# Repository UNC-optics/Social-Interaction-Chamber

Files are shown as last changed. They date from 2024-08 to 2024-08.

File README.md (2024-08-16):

# Detailed Protocol: Social Interaction Chamber 

See the *Detailed Protocol* tab in the *Materials List/Social Interaction Chamber Materials.xlsx* spreadsheet for a sequential list of the required materials for the construction of the Social Interaction Chamber.

GitHub repository: https://github.com/UNC-optics/Social-Interaction-Chamber 

# Construction of laser cut box

1.	Use the *Hardware Manufacturing/Laser Cutting Files/Social Interaction Chamber Walls Laser Cut File.svg* file to vector laser cut the structural panels of the Social Interaction Chamber.
   
2.	Cut the partition and lid (black lines) out of 1/16in clear cast acrylic.
   Clear Laser Cut Pieces
  	
3.	Cut the left and right walls, back wall, and floor (red lines) out of 1/8in white cast acrylic.
   White Laser Cut Pieces
  	
4.	Use acrylic paste cement to attach the walls and floor. Leave the lid and partition detached from the rest of the panels.
   
5.	Use acrylic paste cement to secure the acrylic hinge to the lid and the back wall of the box.
   Chamber Acrylic Assembly

6.	Allow acrylic panels to sit overnight to cure. 

# PCB assembly

7.	Use the *Hardware Manufacturing/PCB Fabrication and Assembly/PCB Fabrication Files Social Interaction Chamber.zip* folder provided in the GitHub to order the custom pre-assembled PCB from a manufacturing company (JLCPCB, HK, CN). The PCB should be prepared as a 1.6mm thick two-layer PCB, with no special instructions.
   
8.	In the same order, use the *Hardware Manufacturing/PCB Fabrication and Assembly/PCB Assembly Files Social Interaction Chamber.zip* folder to request electronic component assembly services. Parts must be placed according to the Bill of Materials and Components Placement List as demonstrated in the assembly files.
    
9.	Following assembly, use a tampered cutter tool to detach the PCB board at the indicated joints to produce 2 L-shaped PCBs and one rectangular PCB.
   PCB PreCut

10. Hand solder the 90-degree pins onto the rectangular PCB as shown.
    PCB PostCut

11. Solder the base of the L-shaped PCBs to the other end of the 90-degree pins to hold them perpendicular to the rectangular PCB. Use the width of the acrylic chamber as a sizing guide and ensure that the diodes of the L-shaped PCBs face inward toward one another with the flush side of the base PCB facing upward.

    PCB Perpendicular

12. Use the tampered cutter tool to trim the excess wire from the 90-degree pins.

# PCB testing and cable construction

13. Plug in a USB-A to USB-C cable into the Seeeduino XIAO and a computer with Arduino IDE software (Version: 2.3.2). Install the Seeeduino library and drivers via the board manager (https://wiki.seeedstudio.com/Seeed_Arduino_Boards/).
    
14. Open the *Microcontroller Programming Code/Programming_Code_Social_Interaction_Chamber.ino* file using the Arduino IDE software. Connect to the Seeeduino XIAO port and allow the device to sit freely without obstructions. Upload the programming code to the board.
  
15. Open the serial monitor in the Arduino software. Obstruct the beam path with a solid object and ensure that Inside “I”, Outside “O”, and Near “N” outputs appear in the serial monitor along with binary data indicating beam break status (0 - no break, 1 - beam broken). Upon functionality confirmation, unplug the device.
    
16. Use wire strippers to remove ~20mm of the outer jacket from one end of the black cable and expose the 4 internal conductors. Then strip ~10 mm of insulator from each of the individual wires to expose the copper core of all internal conductors.
    
17. Thread heat shrink over each of the 4 internal conductors. Hand solder the wires on one side of the cable to each of the metal pins of the 4-pin female socket header as shown in Figure 2B. Pull the heat shrink over exposed wire surfaces and melt the material with a soldering iron to enclose the soldered junctions.
    
    Cable Pinout

18. On the other end of the black cable, use the wire stripper to remove ~50mm of the jacket and ~15mm of insulator from each internal conductor. The open wires will be secured into the ANY-maze digital interface terminals in the experimental protocol.

# 3D printed case and waterproofing
19. 3D print the PCB case and diode sleeves provided in the *Hardware Manufacturing/3D Printed Parts* folder using white PLA filament with 0.2mm resolution.
20. When the print is complete, use tweezers to remove internal supports from the diode sleeves and the PCB case.
    3D Printed Casing
    
21. Place the external PCB case over the finalized PCB to protect the PCB and components.
PCB with Case

22. Fit the PCB around the acrylic walls with the diodes aligned with the 4 holes through each wall. Be sure to avoid dragging the diodes across the edge of the wall to prevent damage.
    
    PCB Placed Around Chamber

23. Super glue the 3D printed inner diode sleeves to the internal wall of the chamber.
    Inner Diode Sleeve Placement

24. With a 1:1 ratio, mix 20mL of 2-part epoxy. If a 1:1 ratio is not maintained, the epoxy will not fully cure.
25. Use a cotton swab to apply the mixed epoxy into the space between the PCB and the external casing, as well as along the bottom edge of the chamber and PCB. Be generous along this surface and over the PCB, as it will waterproof the chamber to prevent potential damage to the PCB caused by mouse urine.
26. While the epoxy is still wet, place the partition over the open face of the chamber. You may also apply epoxy at the top of the side walls to secure the partition in place.

    Partition Placement

27. Place the outer sleeves over the protruding PCB arms and use super glue to secure the sleeves to the outside of the partition.
    Outer Sleeve Placement

28. Allow the chamber to cure for at least an hour before testing. 

# ANY-maze integration

29. To integrate the device with ANY-maze, connect the wires that correspond with the outputs to separate ports in the ANY-maze Digital Interface.
    
30. Connect the ground wire to a secondary terminal in one of the ports.
    
31. In the ANY-maze device configuration settings, configure the selected ports to be TTL inputs with 0V (GND) provided as the output power at the second pin of each port
    
32. Plug in the USB-C to provide 5V of power to the device from the computer and select the I/O tab in ANY-maze to track the status of each output.
  
33. Use a solid object to obstruct the photo beams and test functionality. The default programming outputs trigger a TTL input switch in the following conditions: when the stimulus mouse breaks both beams (Inside - “I”), when the experimental mouse breaks both beams (Outside - “O”), or when the experimental mouse is approaching and breaks only one beam (Near - “N”). Additionally, each N, I, O state is streamed through the USB port whenever a status change occurs and can be used to troubleshoot the ANY-maze integration functionality.

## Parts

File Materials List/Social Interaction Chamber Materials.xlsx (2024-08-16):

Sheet: Detailed Protocol
Hardware List for Step By Step Construction Protocol
RESOURCE | SOURCE | IDENTIFIER | QUANTITY
Chamber Lid | Laser Cut | 1/16 in Clear Acrylic | 1
Chamber Partition | Laser Cut | 1/16 in Clear Acrylic | 1
Chamber Side Walls | Laser Cut | 1/8 in White Acrylic | 2
Chamber Back Wall | Laser Cut | 1/8 in White Acrylic | 1
Chamber Floor | Laser Cut | 1/8 in White Acrylic | 1
Weld-On Acrylic Paste Cement | Amazon | AD37 | 1
Acrylic Hinges | Amazon | 44843-TPFHT-30x33-16 | 1 (16 pcs)
PCB Board | PCB Mill | 1.6mm thick two-layer PCB | 1
Cutter Tool | HAKKO | CHP-170-A | 1
Solder Station | HAKKO | FX888D-23BY | 1
Lead Free Solder Wire | Amazon | B07Q167J98 | 1
Right Angle Pins | DigiKey | PH1RB-18-UA | 1
USB-A to USB-C Cable | DigiKey | 2987-DH-20M50053-ND | 1
Wire Stripper | Amazon | 92644740473 | 1
4-Conductor Cable (1m) | DigiKey | T1288-1-ND | 1
Heat Shrink Tubing | DigiKey | FP-KIT-ND | 1 (350 pcs)
4-pin female socket header | DigiKey | 732-61300411821-ND | 1
Inside Light Sleeves | 3D-Print | White PLA (0.2mm resolution) | 2
Outside Light Sleeves | 3D-Print | White PLA (0.2mm resolution) | 2
External PCB Case | 3D-Print | White PLA (0.2mm resolution) | 1
Tweezers | Amazon | KA-003 | 1 (3 pcs)
Super Glue | Amazon | B00HYDYSLI | 1
2-part Epoxy | Amazon | B001Z3C3AG | 1
Cotton Swabs | Amazon | B09X2Y4946 | 1 (500 pcs)

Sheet: Resources
Chamber Construction Protocol
RESOURCE | SOURCE | IDENTIFIER | QUANTITY
Acrylic Hinges | Amazon | 44843-TPFHT-30x33-16 | 1 (16 pcs)
Tweezers | Amazon | KA-003 | 1 (3 pcs)
Cotton Swabs | Amazon | B09X2Y4946 | 1 (500 pcs)
Wire Stripper | Amazon | 92644740473 | 1
Super Glue | Amazon | B00HYDYSLI | 1
Weld-On Acrylic Paste Cement | Amazon | AD37 | 1
Lead Free Solder Wire | Amazon | B07Q167J98 | 1
2-part Epoxy | Amazon | B001Z3C3AG | 1
Heat Shrink Tubing | DigiKey | FP-KIT-ND | 1 (350 pcs)
Right Angle Pins | DigiKey | PH1RB-18-UA | 1
USB-A to USB-C Cable | DigiKey | 2987-DH-20M50053-ND | 1
4-Conductor Cable (1m) | DigiKey | T1288-1-ND | 1
4-pin female socket header | DigiKey | 732-61300411821-ND | 1
Cutter Tool | HAKKO | CHP-170-A | 1
Solder Station | HAKKO | FX888D-23BY | 1
Experimental Protocol
RESOURCE | SOURCE | IDENTIFIER | QUANTITY
Modular Fear Conditioning Chamber | MedAssociates | ENV-007-VP | 1
Modular Fear Conditioning Chamber Grid Floor | MedAssociates | ENV-005A | 1
ANY-maze Animal Shocker | Stoelting Co | 60001-51 | 1
ANY-maze Digital Interface | Stoelting Co | 60064 | 1
C57BL/6 Mice | UNC Animal Models Core Facility | N/A | 23

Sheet: Custom Materials
Custom Electrical Components
RESOURCE | FABRICATION | SPECIFICATIONS | QUANTITY
PCB Board | PCB Mill | 1.6mm thick two-layer PCB | 1
Custom Mechanical Components
RESOURCE | FABRICATION | SPECIFICATIONS | QUANTITY
Chamber Lid | Laser Cut | 1/16 in Clear Acrylic | 1
Chamber Partition | Laser Cut | 1/16 in Clear Acrylic | 1
Chamber Side Walls | Laser Cut | 1/8 in White Acrylic | 2
Chamber Back Wall | Laser Cut | 1/8 in White Acrylic | 1
Chamber Floor | Laser Cut | 1/8 in White Acrylic | 1
Inside Light Sleeves | 3D-Print | White PLA (0.2mm resolution) | 2
Outside Light Sleeves | 3D-Print | White PLA (0.2mm resolution) | 2
External PCB Case | 3D-Print | White PLA (0.2mm resolution) | 1

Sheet: Software
Software and Support Packages
RESOURCE | SOURCE | IDENTIFIER | USE
Arduino IDE (Version 2.3.2) | Arduino | https://www.arduino.cc/en/software | Microcontroller programming
Seeduino Board Manager (Arduino IDE) | Seeed Studio | https://wiki.seeedstudio.com/Seeed_Arduino_Boards/ | Microcontroller programming
AnyMaze (Version 7.4) | AnyMaze | https://www.any-maze.com/support/downloads/ | Data collection
GraphPad Prism (Version 10.2.2) | GraphPad | https://www.graphpad.com/ | Data analysis

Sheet: PCB BOM
PCB Bill of Materials (Included in PCB Assembly Files Folder)
NAME | QUANTITY | MANUFACTURER IDENTIFIER | PCB DESIGNATOR | PCB FOOTPRINT | PCB DESIGNATION
Seeeduino XAIO | 1 | 102010328 | U1 | Seeeduino XIAO-MOUDLE14P-2.54-21X17.8MM | SeeeduinoXIAO
Lm321 Op Amp | 4 | LM321MFX/NOPB | U5, U6, U7, U9 | SOT-23-5 | LM321
MOSFET | 7 | AOSS21311C | Q1,Q2,Q3,Q4,Q5,Q6,Q7 | SOT-23 | AO4300
IR LED | 4 | APT2012F3C | D2,D3,D4,D5 | LED_0805_2012Metric | LED
IR Photodiode | 4 | B17M1PD--H9B000114U1930 | D6,D7,D8,D9 | LED_0805_2012Metric | D_Photo
100k Ohm Resistor | 7 | ERJ-6ENF1003V | R1,R4,R6,R13,R15,R17,R19 | R_0805_2012Metric | 100k
91 Ohm Resistor | 4 | ERJ-6ENF91R0V | R5,R11,R12,R14 | R_0805_2012Metric | 90
5.1M Ohm Resistor | 4 | ERJ-6GEYJ515V | R7,R8,R9,R10 | R_0805_2012Metric | 5M
220 Ohm Resistor | 3 | ERJ-6ENF2200V | R16, R18, R20 | R_0805_2012Metric | 220

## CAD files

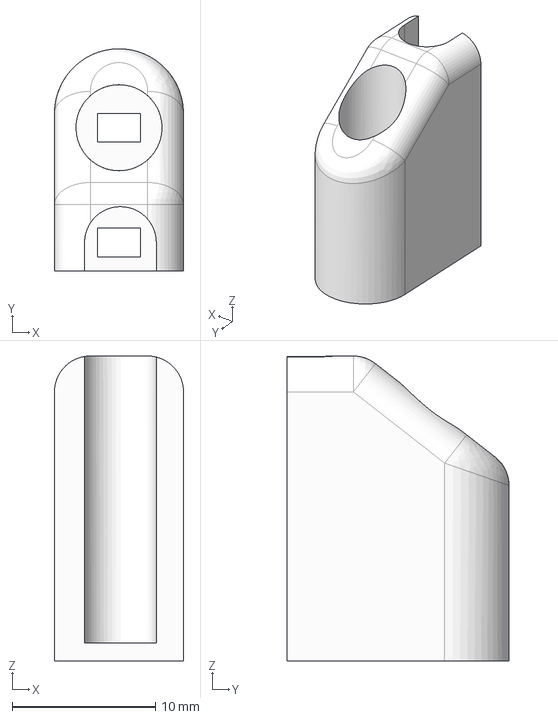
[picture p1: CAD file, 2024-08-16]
Hardware Manufacturing/3D Printed Parts/Left Inner Sleeve.step
9.00 x 15.5 x 21.3 mm

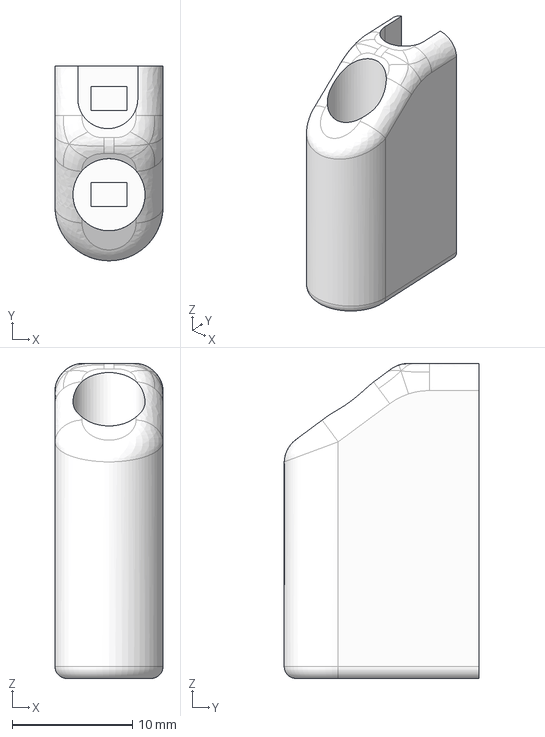
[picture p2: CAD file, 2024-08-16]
Hardware Manufacturing/3D Printed Parts/Left Outer Sleeve.step
9.00 x 16.2 x 26.2 mm

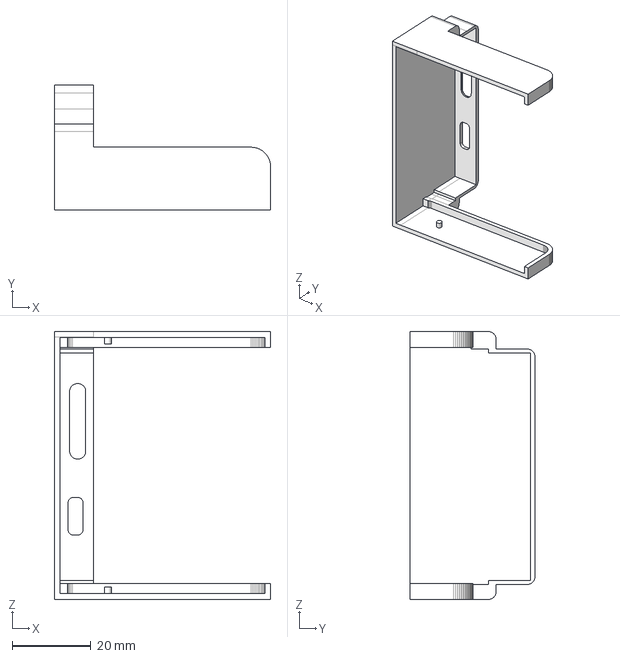
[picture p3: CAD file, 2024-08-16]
Hardware Manufacturing/3D Printed Parts/PCB Case.step
55.1 x 31.8 x 68.3 mm

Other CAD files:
Hardware Manufacturing/3D Printed Parts/Right Inner Sleeve.step
Hardware Manufacturing/3D Printed Parts/Right Outer Sleeve.step

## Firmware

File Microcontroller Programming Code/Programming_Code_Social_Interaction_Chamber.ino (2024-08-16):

// Social Interaction Chamber System
// Developed by the Pegard and Rodriguez-Romaguera labs at UNC-Chapel Hill.

// This Arduino sketch manages a Social Interaction Chamber by monitoring the status of Infrared (IR) beams to detect 
// the presence of experimental and stimulus mice across a window. The system utilizes an array of IR photodiodes
// and LEDs to track interactions and updates the status in real-time via the serial monitor and TTL outputs.

// Key functionalities:
//  - Calibration of IR photodiodes to establish baseline readings.
//  - Continuous monitoring of IR beam disruptions.
//  - Dynamic adjustment of baseline values to account for minor ambient light changes.
//  - Real-time reporting of beam status via serial communication.
//  - Control of output pins based on beam activity to indicate mouse location and movement.

const int PDPins[] = { 7, 8, 6, 5 };  // Pins for IR photodiodes (PDs), outside to inside
const int DPins[] = { 9, 10, 4, 3 };  // Pins for IR LEDs, outside to inside
float highvalues[4];                  // store baseline PD values
int signal[4];                        // status array for each Infrared beam
float propsignal[4];                  // proportional difference between the current and baseline reading of PDs
volatile int measurement = 0;         // current analog PD reading
volatile float drift = 0;             // difference between the current and baseline reading of PDs
const float sensitivity = 50.0;       // INCREASE UP TO 200 IF TOO SENSITIVE
void setup() {
  for (int j = 0; j < 4; j++) {  // configure the pin states
    pinMode(DPins[j], OUTPUT);
    pinMode(PDPins[j], INPUT);
    digitalWrite(DPins[j], HIGH);  // turn all LEDs on
  }
  delay(20);
  for (int j = 0; j < 4; j++) {
    highvalues[j] = 1.0 * analogRead(PDPins[j]);
  }
  for (int jj = 0; jj < 40; jj++) {
    for (int j = 0; j < 4; j++) {
      highvalues[j] = 0.9 * highvalues[j] + 0.1 * analogRead(PDPins[j]);  // calibration: initializes highvalues array by averaging the baseline across 40 readings
    }
  }
  Serial.begin(9600);  // Start serial communication
}
void loop() {
  for (int i = 0; i < 4; i++) {  // monitor PD readings
    measurement = analogRead(PDPins[i]);
    drift = abs(1.0 * measurement - highvalues[i]);
    if (drift < sensitivity) {
      highvalues[i] = 0.999 * highvalues[i] + 0.001 * measurement;  // adjust baseline to account for minor ambient light changes
    }
    propsignal[i] = 0.9 * propsignal[i] + 0.1 * drift;  // update proportional signal to consider current drift
  }
  for (int i = 0; i < 4; i++) {  // update beam break outputs by comparing the proportional signal to sensitivity threshold
    if (propsignal[i] > sensitivity && signal[i] == 0) {
      signal[i] = 1;
      updatestatus();
    }  // print current beam status
    if (propsignal[i] < sensitivity && signal[i] == 1) {
      signal[i] = 0;
      updatestatus();
    }
  }


  void updatestatus() {  // indicates mouse status based on beam activity, updates trigger output values and streams status on serial port

    for (int i = 0; i < 4; i++) {
      Serial.print(signal[i]);
      Serial.print(",");
    }
    if (signal[0] * signal[1] == 1) {
      digitalWrite(0, HIGH);  // stimulus mouse at window (both inside beams broken)
      Serial.print("I");
      Serial.print(",");
    } else {
      digitalWrite(0, LOW);  // stimulus mouse not at window (none or only one inside beam broken)
      Serial.print("-");
      Serial.print(",");
    }
    if (signal[2] * signal[3] == 1) {
      digitalWrite(1, HIGH);  // experimental mouse at window (both outside beams broken)
      Serial.print("O");
      Serial.print(",");
    } else {
      digitalWrite(1, LOW);  // experimental mouse not at window (none or only one outside beam broken)
      Serial.print("-");
      Serial.print(",");
    }
    if (signal[3] >= 1) {
      digitalWrite(2, HIGH);  // experimental mouse approaching window (one outside beam broken)
      Serial.println("N");
    } else {
      digitalWrite(2, LOW);  // experimental mouse not near or approaching window (no outside beams broken)
      Serial.println("-");
    }
  }
